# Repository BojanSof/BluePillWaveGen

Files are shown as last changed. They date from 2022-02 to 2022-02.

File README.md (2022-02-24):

# STM32 BluePill DDS WaveGen

DDS function generator implemented with STM32 BluePill board, based on
STM32F103C8T6 microcontroller, 8-bit R-2R ladder DAC and additional circuitry
for removing the DC offset.

The user interface is realized with OLED display based on SSD1306 controller and
incremental rotary encoder.

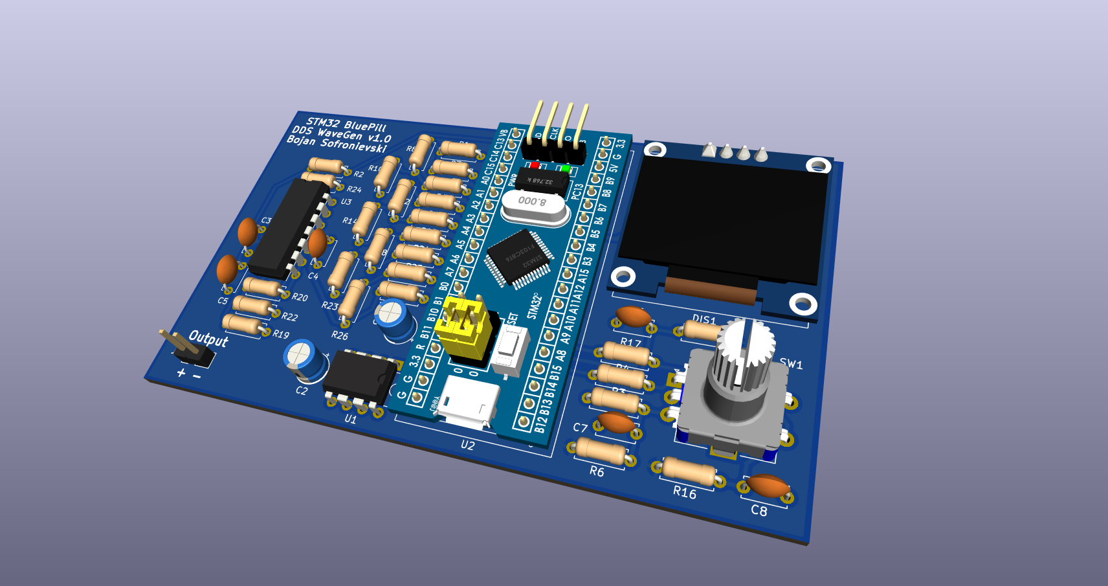
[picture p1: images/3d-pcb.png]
Kicad PCB 3D view


## Specs

Goal specs:

- Waveforms: sine, square, triangle, sawtooth (arbitrary waveforms can easily be
  added)
- Frequency: 0 - 35 kHz, frequncy resolution is variable
- Amplitude: 500 - 3000 mV (software control)

Additional tests and modifications should be done to reach the specs.

## Working Principle

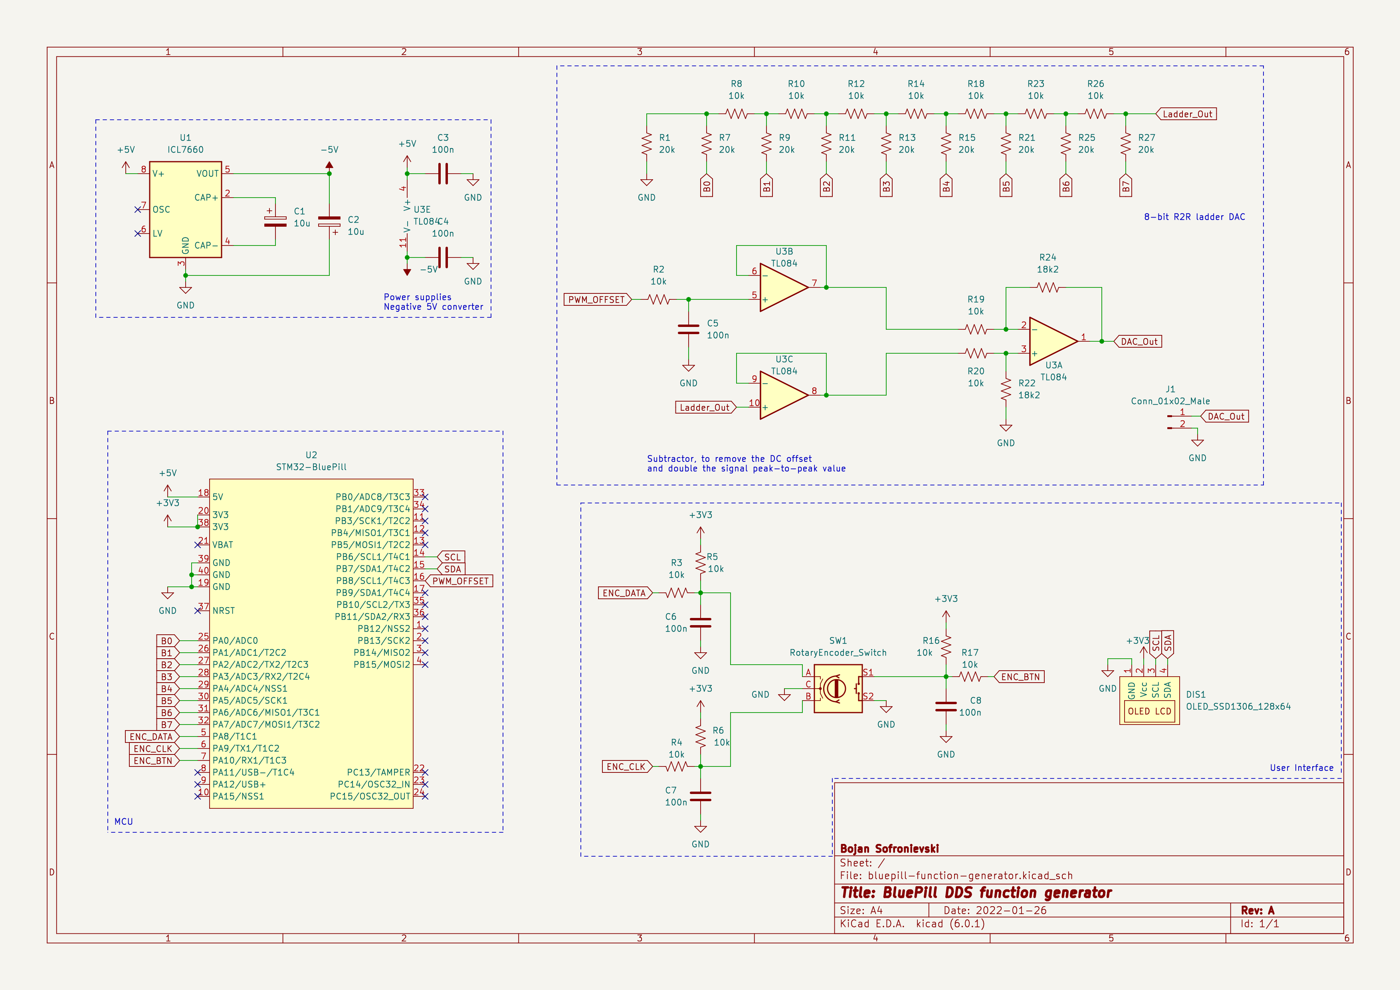
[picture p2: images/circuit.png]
WaveGen circuit


The MCU generates the data for the 8-bit R-2R ladder D/A converter.

Two of the op amps inside TL084 are used as voltage buffers, one for the output
of the DAC and the second one for the variable voltage generated by filtering
PWM signal outputed by the MCU.
This variable voltage is used to remove the DC offset of the generated waveform.
Removing the DC offset is realised with the third op amp, which subtracts the
output of the DAC and the variable voltage and multiplies this difference by
1.82 so the output signal has maximum amplitude of 3 V.

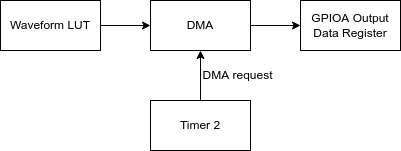
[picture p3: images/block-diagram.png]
DAC data generation


To generate the data for the DAC, each waveform has lookup table stored in the
Flash memory of the MCU, with 256 elements with size 1 byte.
The values stored in the table are actually the data that need to be fed into
the DAC.
During runtime, whole or part of the table is copied into SRAM of the MCU, based
on the frequency of the waveform.
By changing the LUT, arbitrary periodic waveforms can be generated.

Timer 2 of the MCU is configured to generate DMA request.
It has base clock of  14.4 MHz and the value stored in the Auto-Reload Register 
(ARR) depends on the  frequency of the waveform. The value for ARR is calculated
using the following formula:

<center>ARR=TIM2\_BaseClock/(L\*f) - 1</center>

where L is the size of the LUT stored in SRAM and f is the frequency of the
waveform.

The DMA unit transfers data from the LUT in SRAM to the GPIOA output data
register.
The pins PA0-PA7 are used to output the data to the DAC.
Because the output data register of GPIOA is used, the pins PA8-PA15 can not be
used as general purpose outputs, but can be used in the other modes.
This problem can be resolved by writing to the bit set reset register instead of
the output data register.

## Software

The software was written in C, using STM32 HAL library, in STM32CubeIDE.

I have also written SSD1306 driver which can be further developed to include
more functionalities.

The code also includes isntantenous rotational speed measurement for the rotary
encoder with goal to change the values for frequency and amplitude based on the
rotational speed, i.e. faster turning of the encoder results in greater change
of the value.
This part of the code should also be improved, for better user experience.

## Experimental results

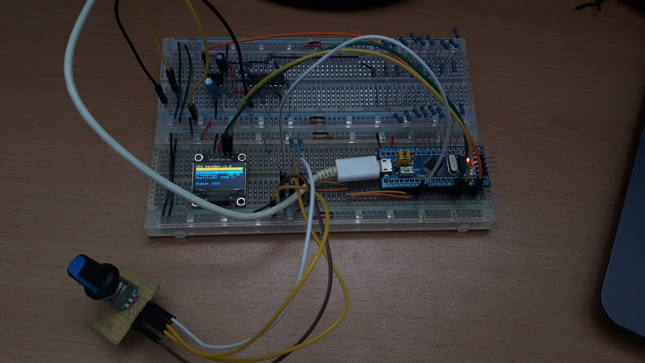
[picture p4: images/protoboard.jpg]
Protoboard version


The following waveforms are measured with DSO150 oscilloscope.

<table>
  <tr>
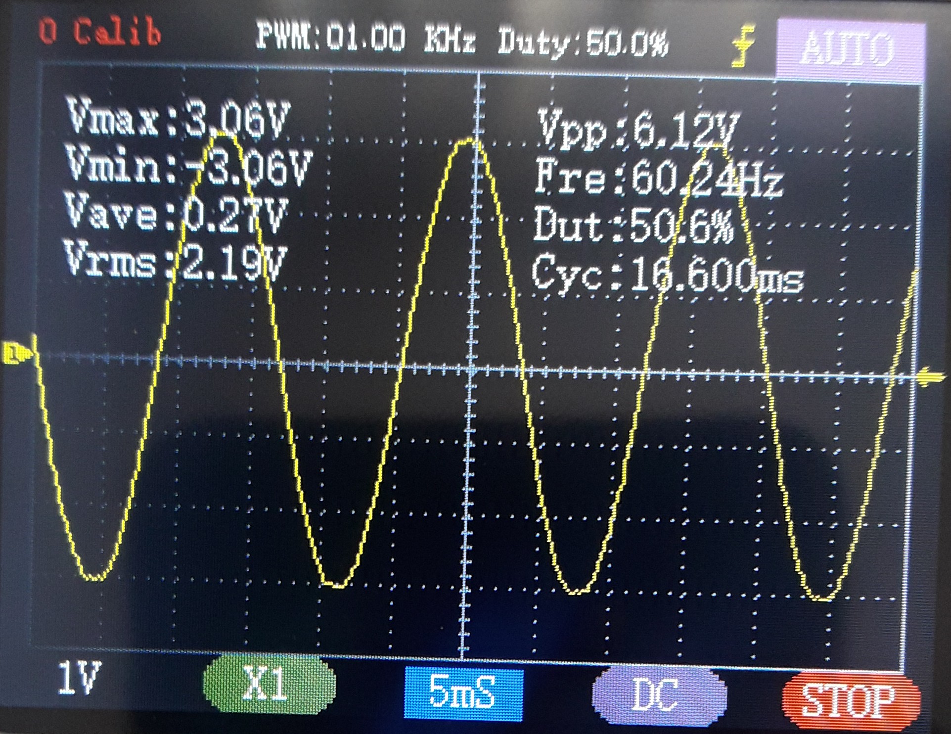
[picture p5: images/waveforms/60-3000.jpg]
Sine 60 Hz 3000 mV
    <td> </td>
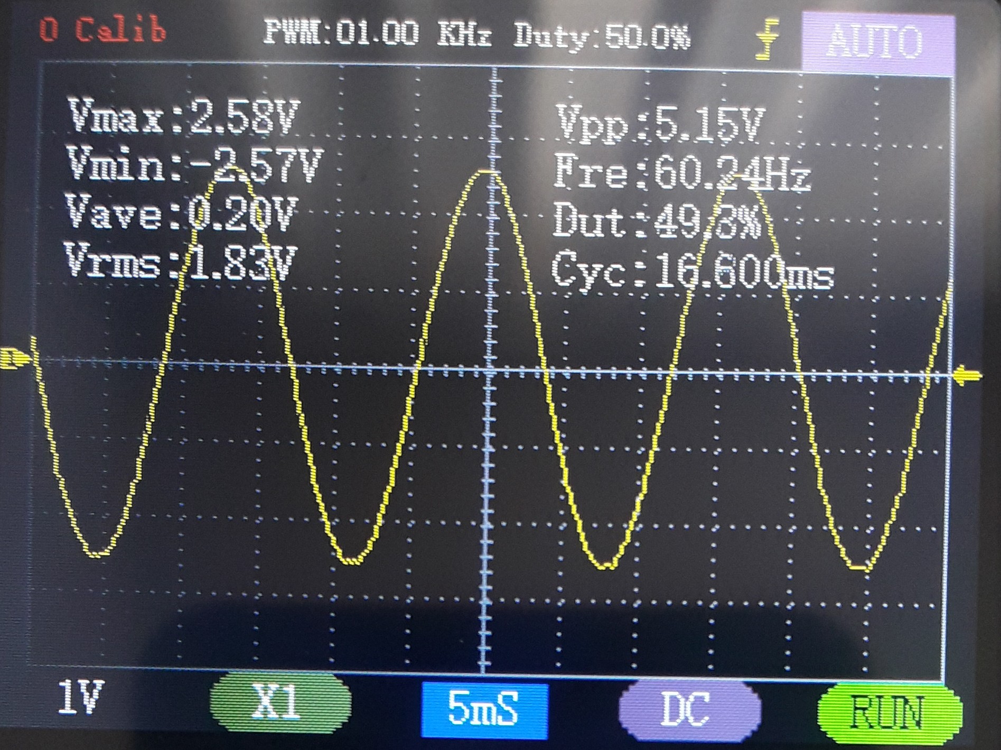
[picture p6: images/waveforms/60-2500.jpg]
Sine 60 Hz 2500 mV
    <td> </td>
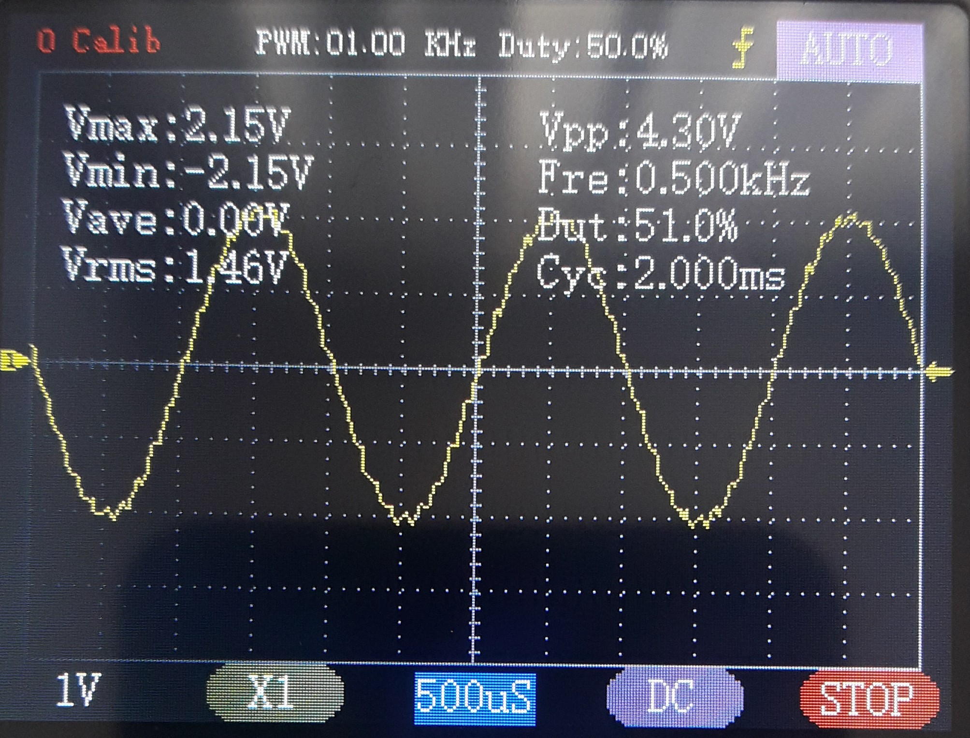
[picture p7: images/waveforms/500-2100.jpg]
Sine 500 Hz 2100 mV
    <td> </td>
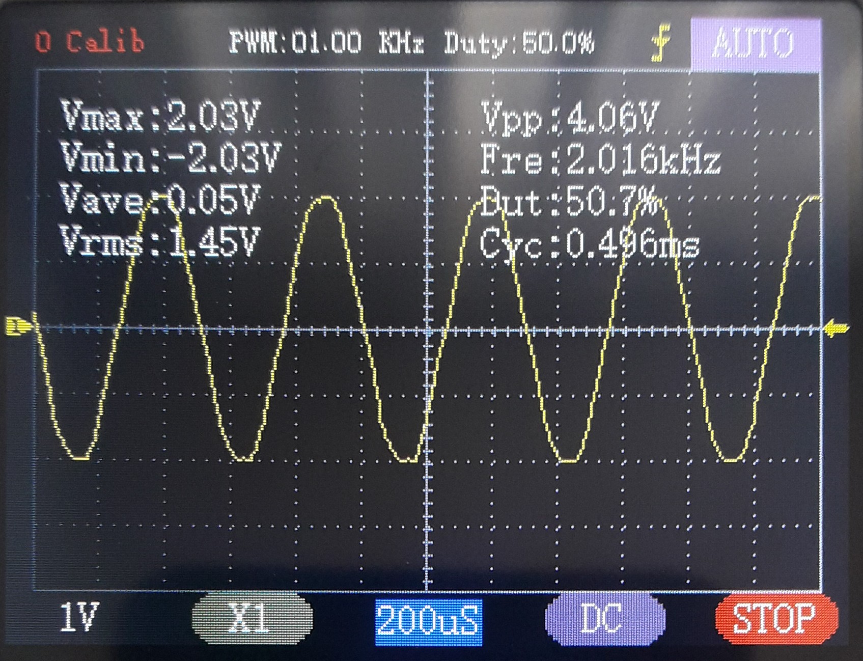
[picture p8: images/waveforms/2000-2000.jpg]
Sine 2000 Hz 2000 mV
    <td> </td>
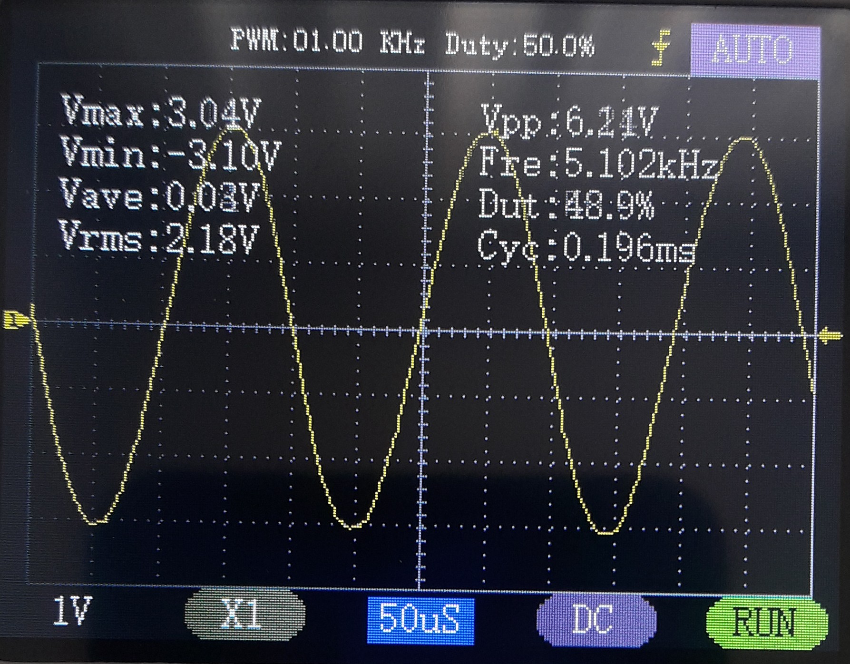
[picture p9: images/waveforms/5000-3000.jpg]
Sine 5000 Hz 3000 mV
    <td> </td>
  </tr> 
  <tr>
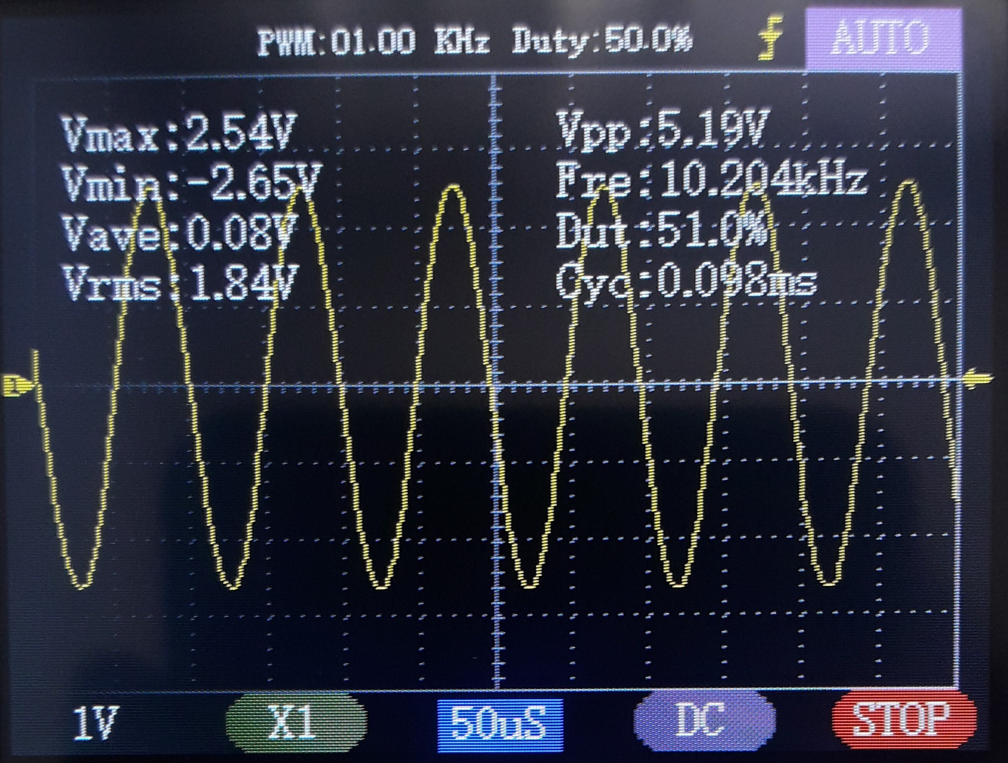
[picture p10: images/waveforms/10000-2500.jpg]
Sine 10000 Hz 2500 mv
    <td> </td>
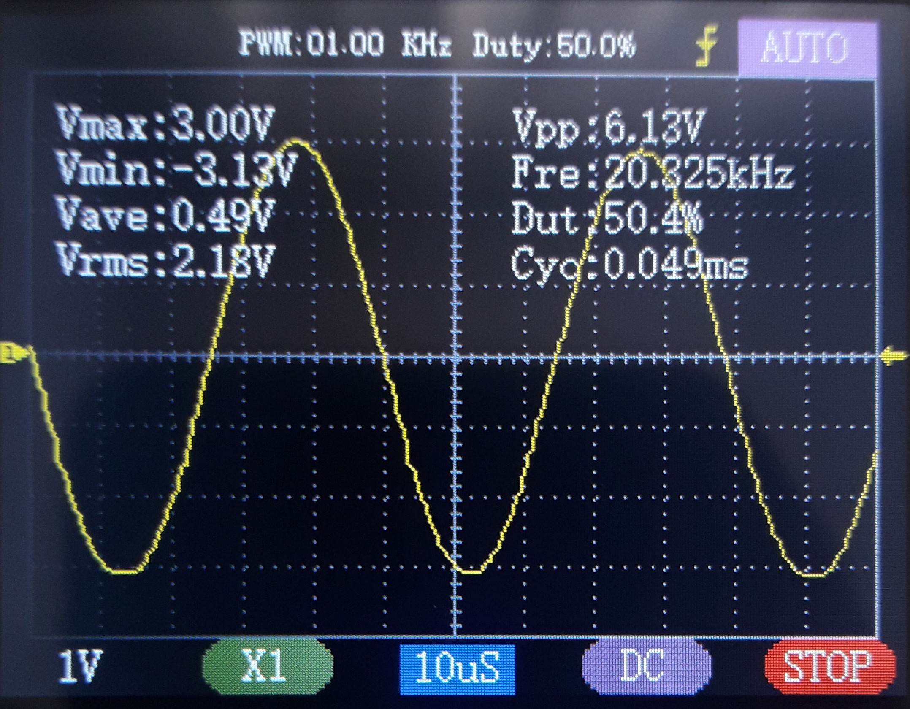
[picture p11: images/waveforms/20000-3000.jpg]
Sine 20000 Hz 3000 mv
    <td> </td>
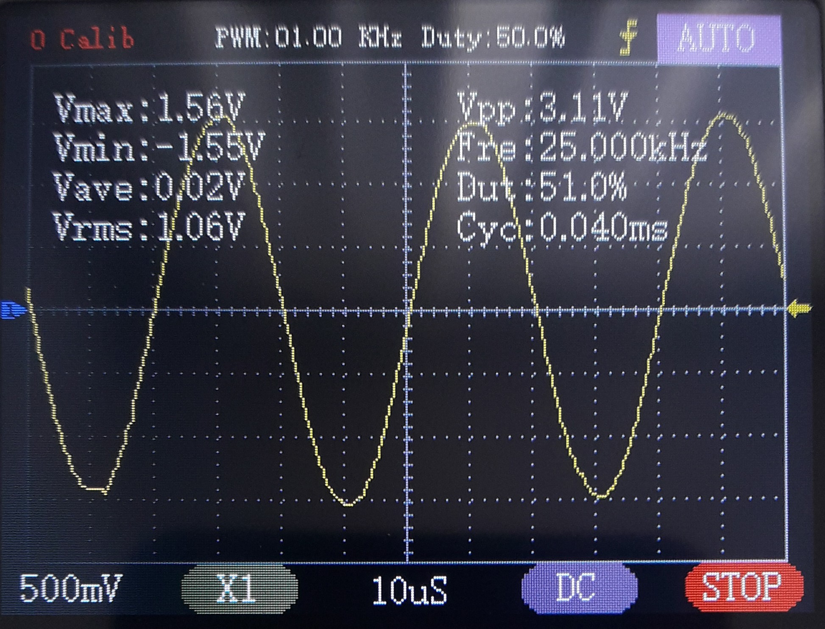
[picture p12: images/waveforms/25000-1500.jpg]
Sine 25000 Hz 1500 mv
    <td> </td>
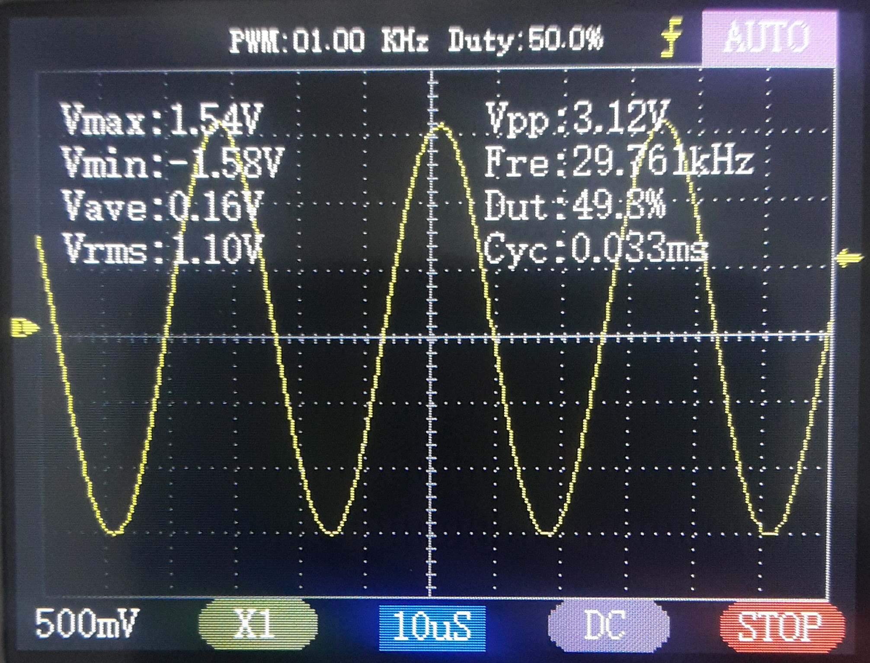
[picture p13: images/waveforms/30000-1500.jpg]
Sine 30000 Hz 1500 mv
    <td> </td>
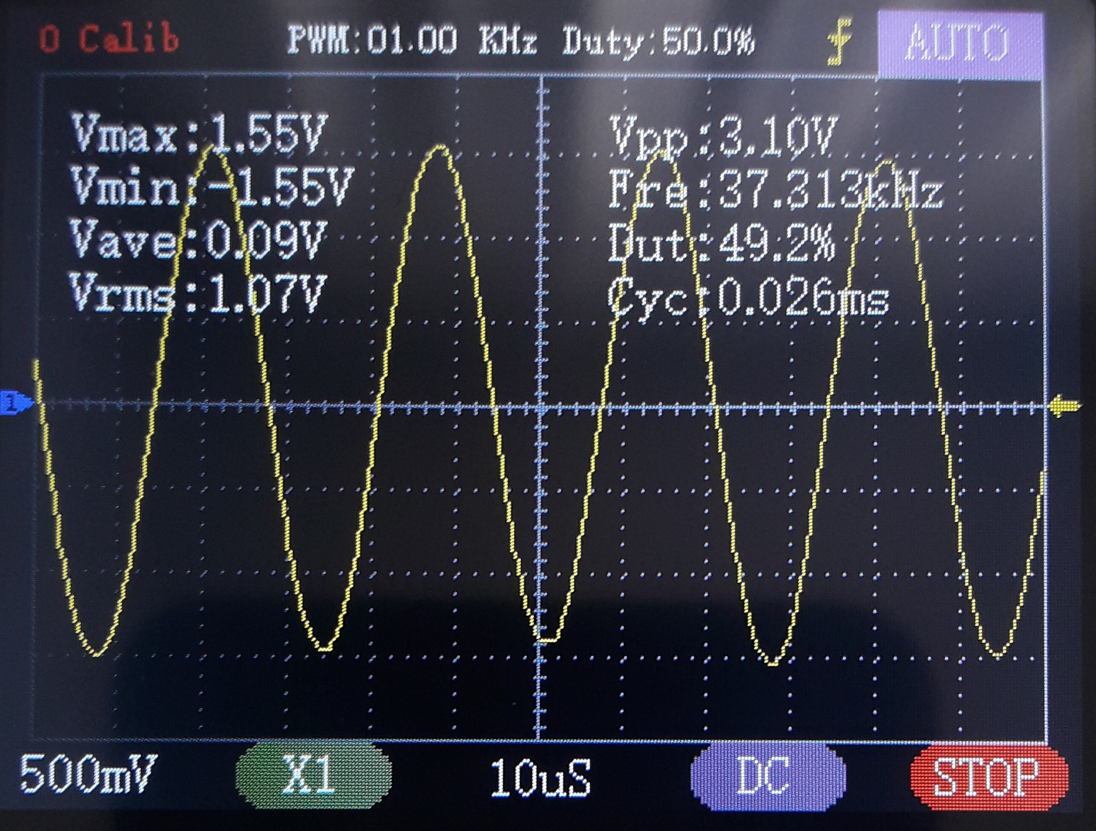
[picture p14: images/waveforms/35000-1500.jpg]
Sine 35000 Hz 1500 mv
    <td> </td>
  </tr> 
  <tr>
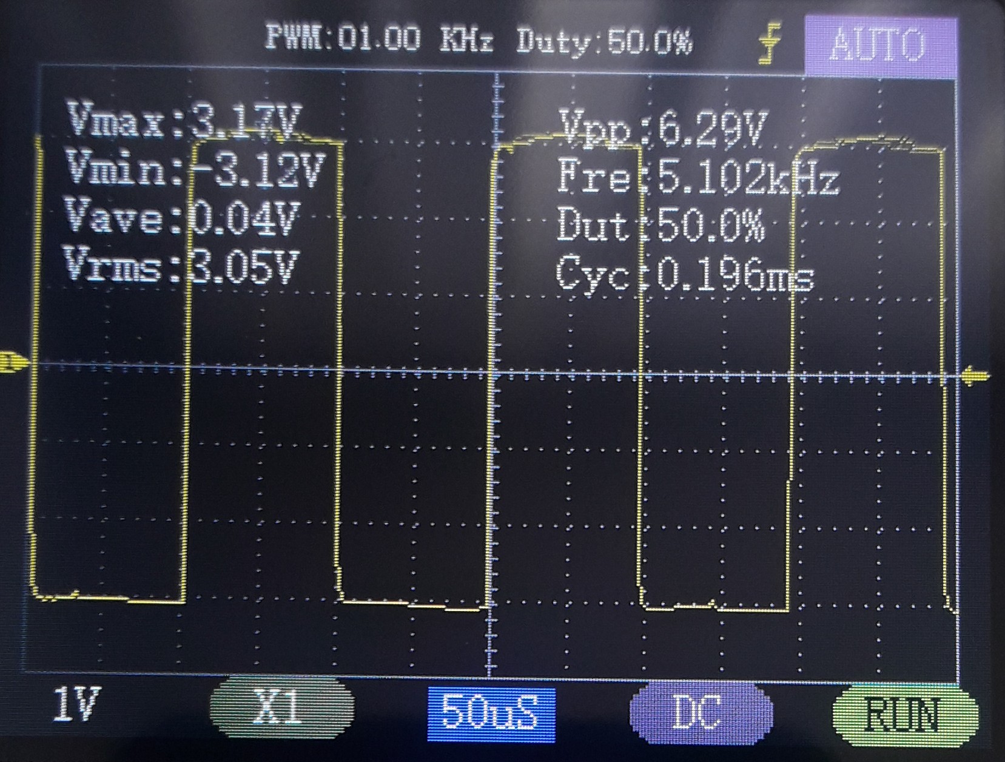
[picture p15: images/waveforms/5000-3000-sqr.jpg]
Square 5000 Hz 3000 mv
    <td> </td>
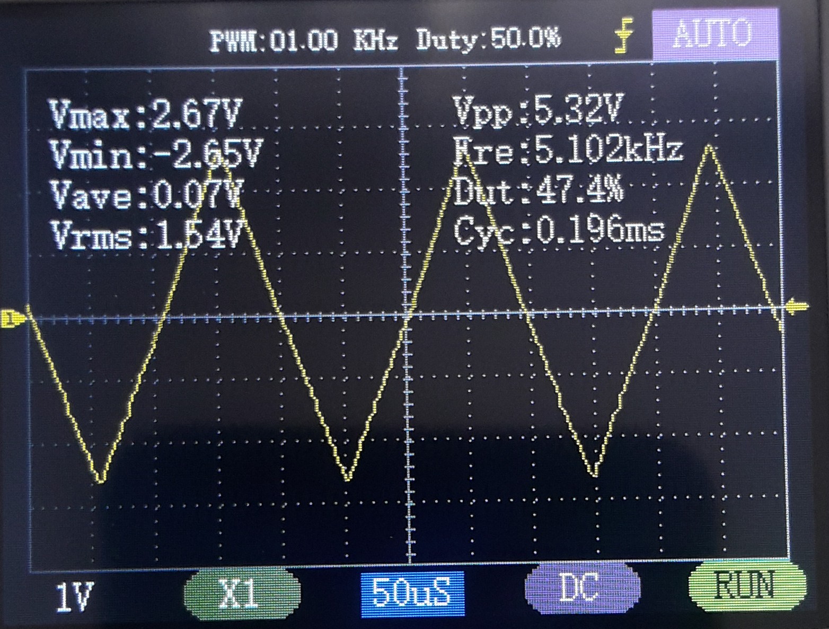
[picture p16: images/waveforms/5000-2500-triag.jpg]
Triangle 5000 Hz 2500 mv
    <td> </td>
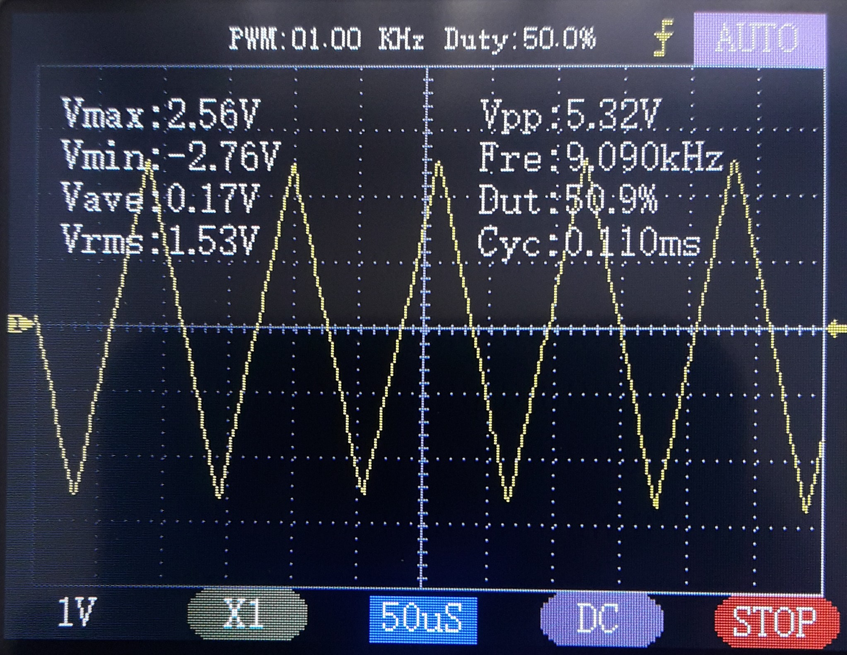
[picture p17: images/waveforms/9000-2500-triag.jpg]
Triangle 9000 Hz 2500 mv
    <td> </td>
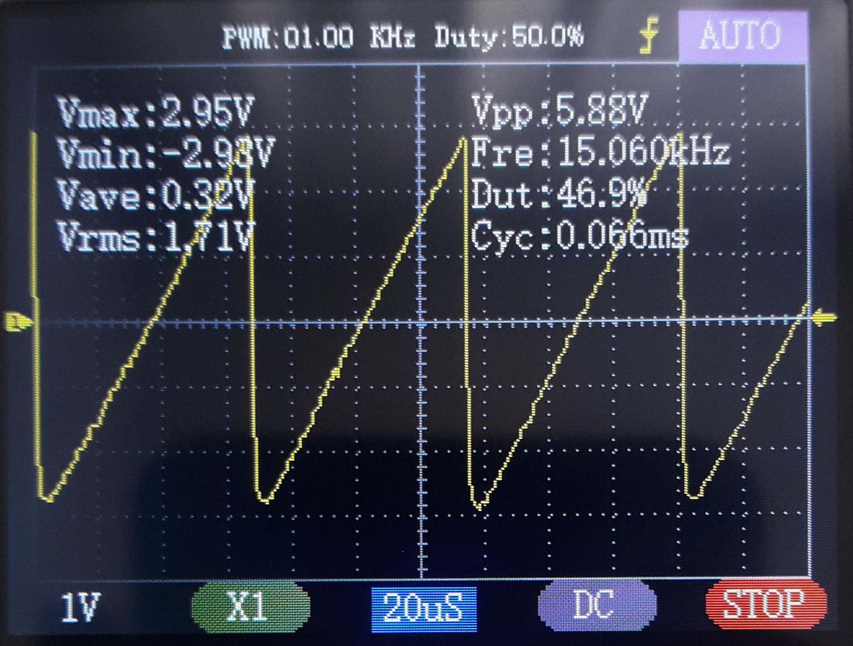
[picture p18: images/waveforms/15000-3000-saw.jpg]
Sawtooth 15000 Hz 3000 mv
    <td> </td>
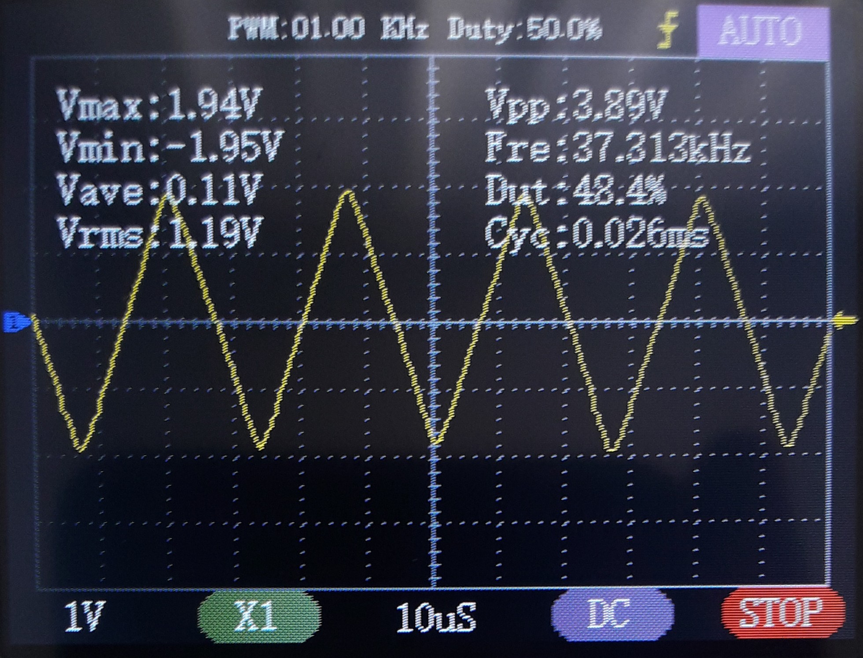
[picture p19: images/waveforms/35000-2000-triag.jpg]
Triangle 35000 Hz 2000 mv
    <td> </td>
  </tr> 
</table>

## Further improvements

- Additional tests and calibration to conclude the frequency and amplitude resolution
- USB virtual serial port to transfer LUT data for arbitrary waveform
- Low-pass filter after DAC output

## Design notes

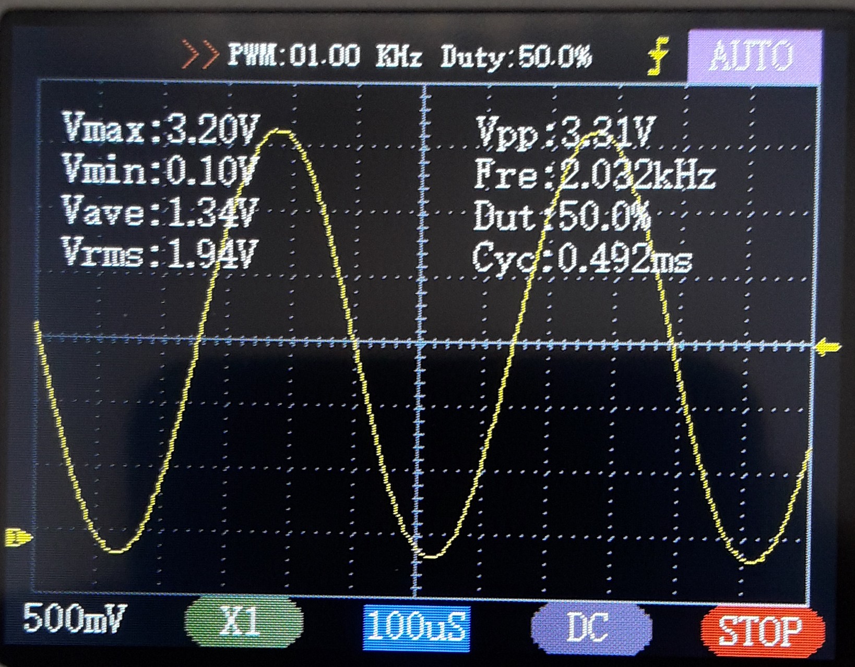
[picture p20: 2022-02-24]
images/waveforms/2000-r2r.jpg

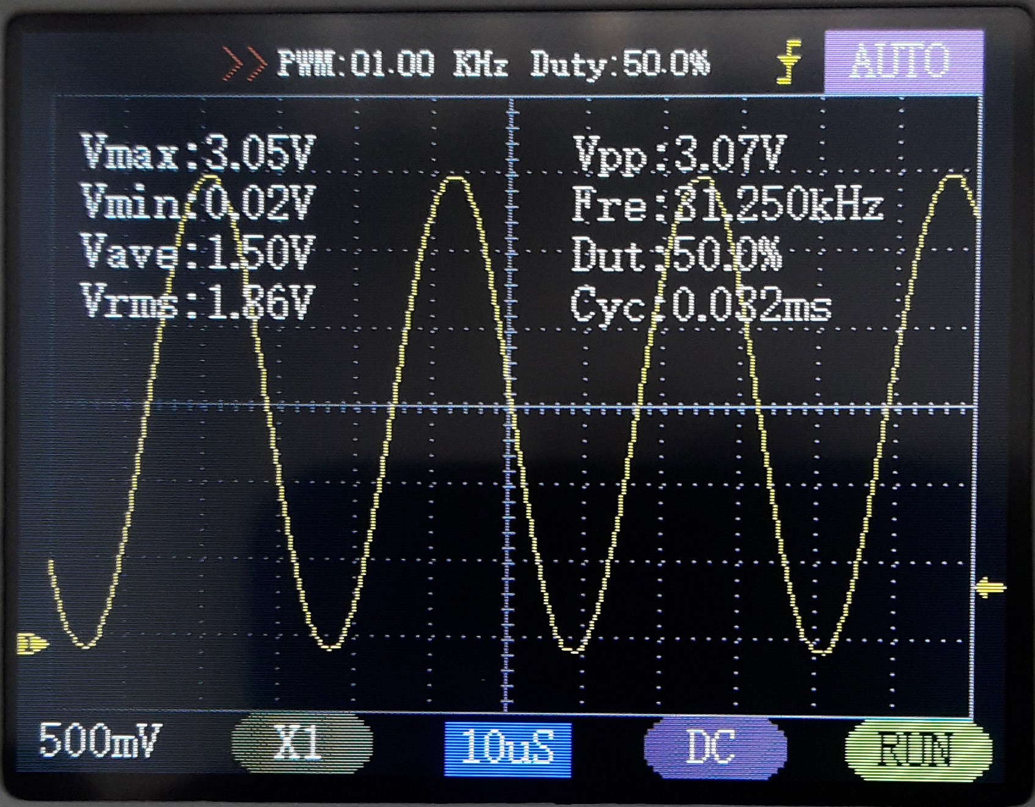
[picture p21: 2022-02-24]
images/waveforms/29900-r2r.jpg

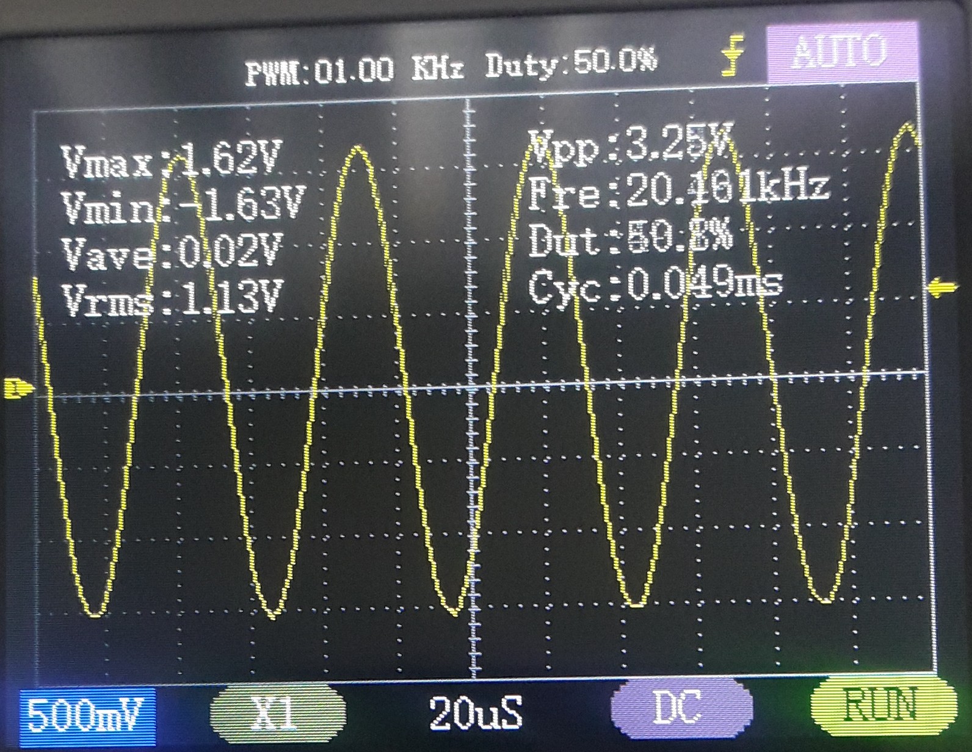
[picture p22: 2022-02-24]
images/waveforms/20000-r2r.jpg

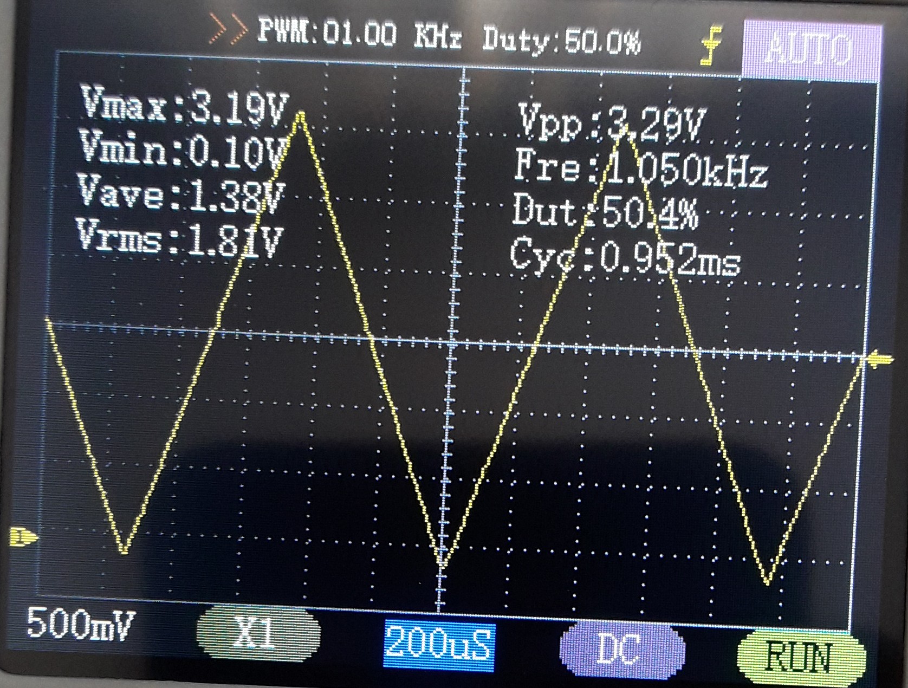
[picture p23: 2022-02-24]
images/waveforms/1050-r2r-triag.jpg

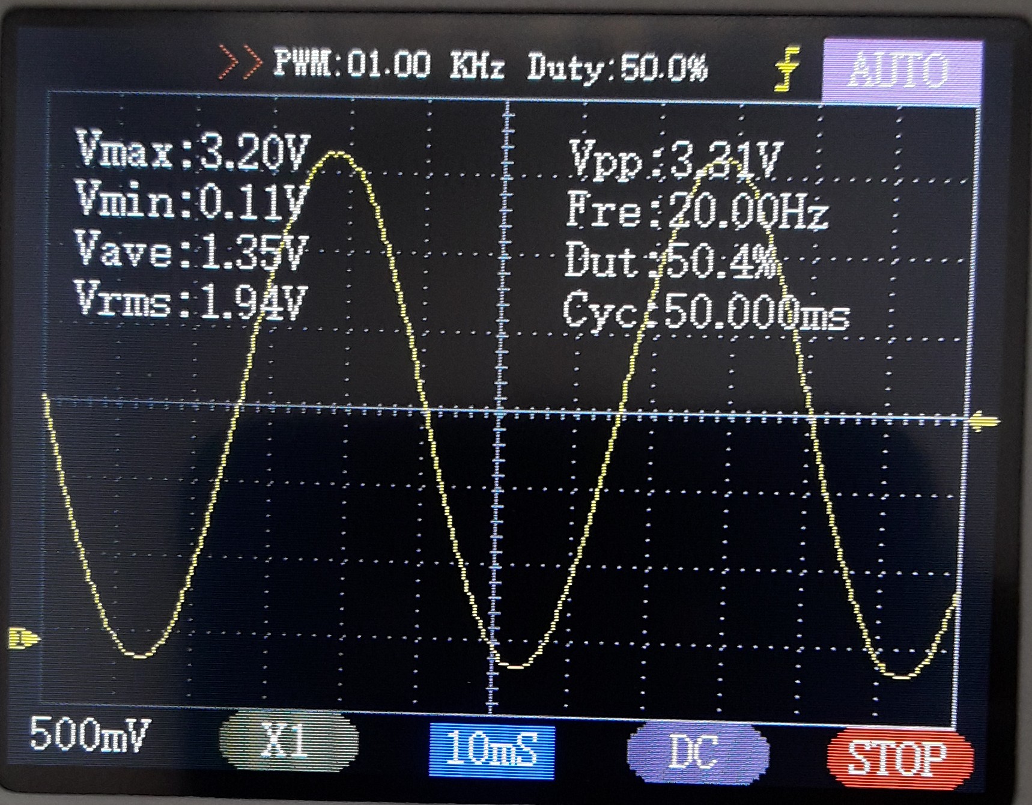
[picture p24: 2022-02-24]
images/waveforms/20-r2r.jpg

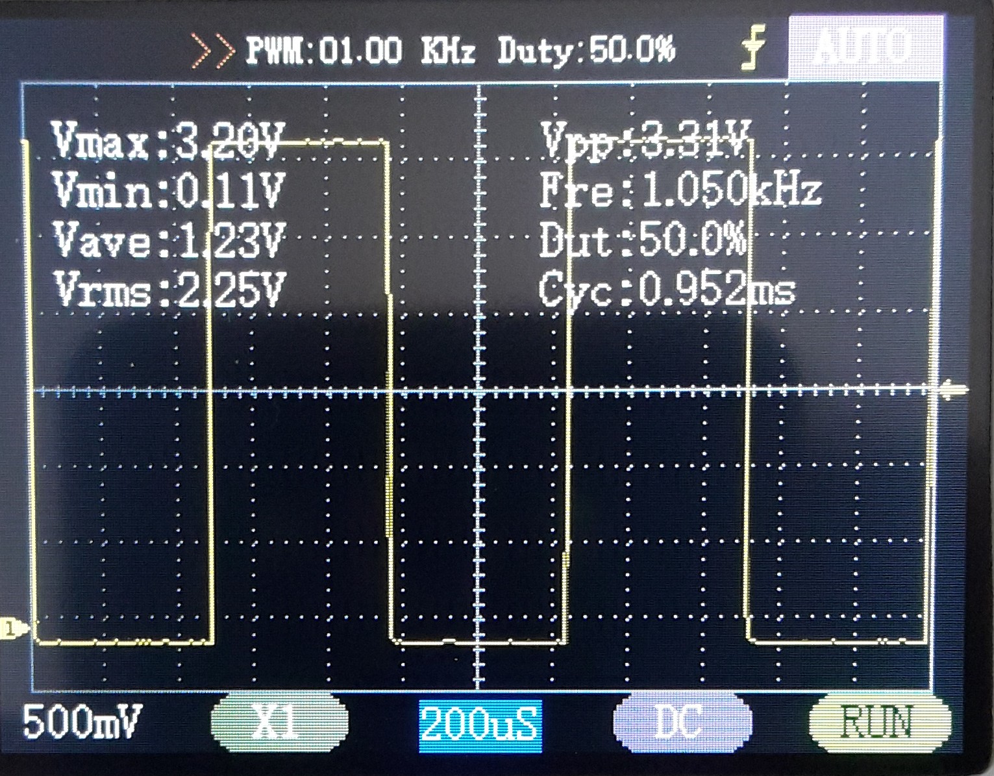
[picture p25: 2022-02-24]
images/waveforms/1050-r2r-sqr.jpg

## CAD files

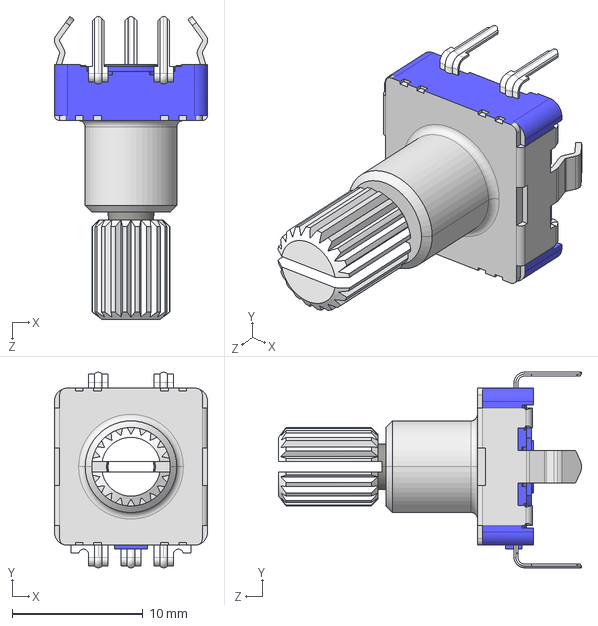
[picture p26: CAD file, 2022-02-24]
kicad/bluepill-function-generator/3d-models/RotaryEncoder/EC11RotaryEncoderSwitch-15mm.STEP
11.7 x 15.0 x 23.2 mm

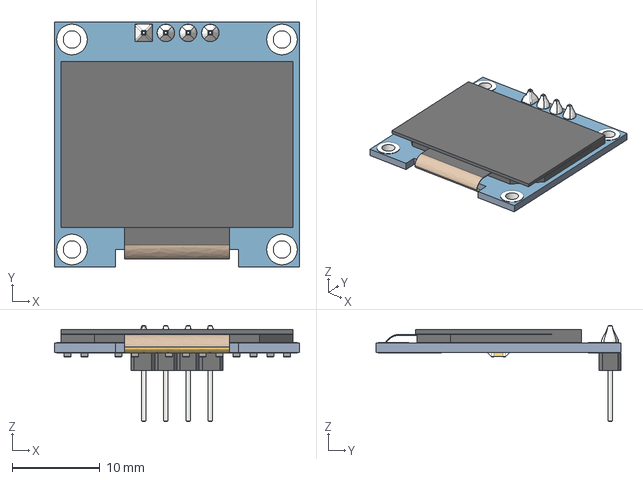
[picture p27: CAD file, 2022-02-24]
kicad/bluepill-function-generator/3d-models/SSD1306-OLED-I2C/OLEDv3.step
28.0 x 28.0 x 11.0 mm

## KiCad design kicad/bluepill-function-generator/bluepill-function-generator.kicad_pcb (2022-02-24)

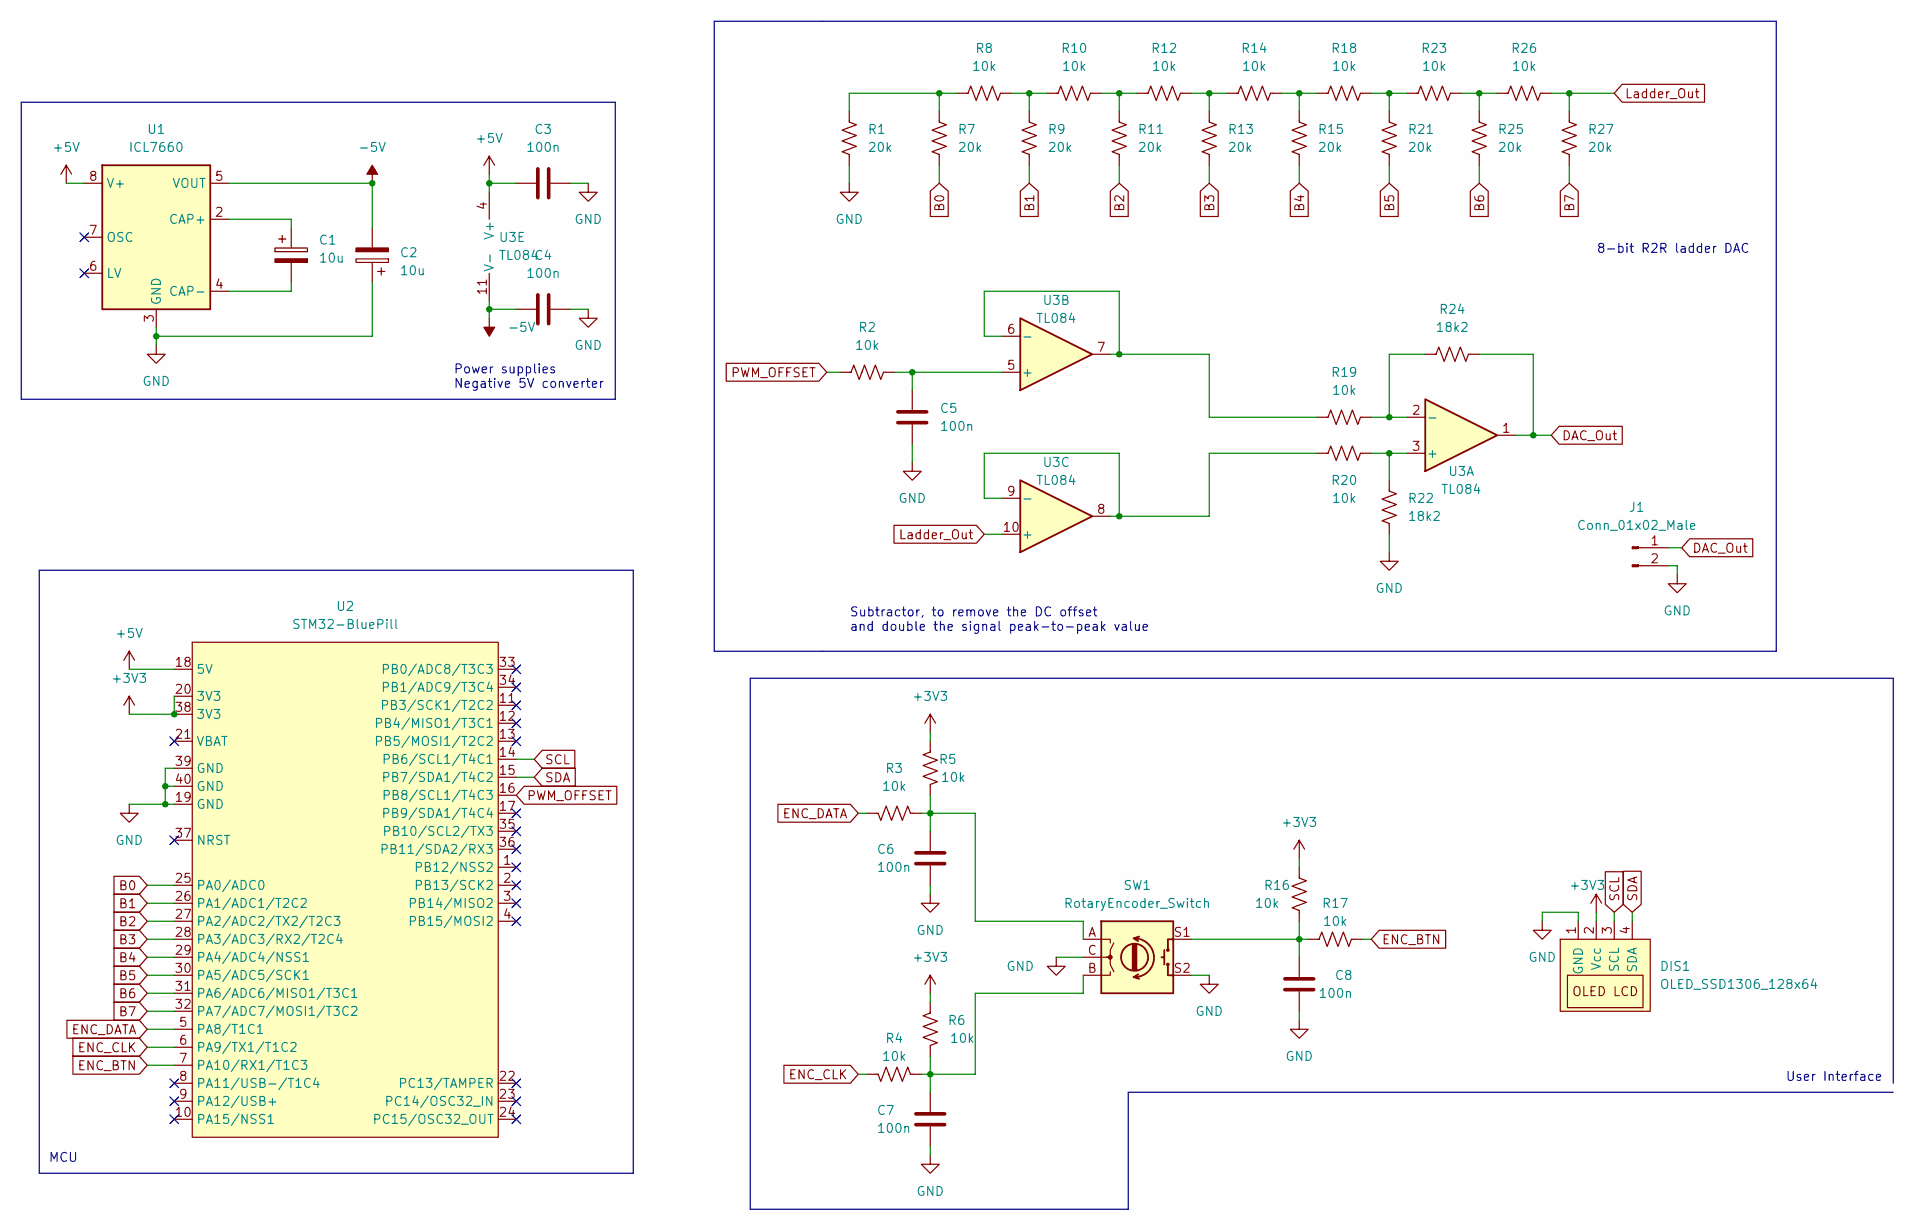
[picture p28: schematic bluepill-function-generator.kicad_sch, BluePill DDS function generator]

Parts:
C1, C2: 10u; CP_Radial_D5.0mm_P2.50mm
C3, C4, C5, C6, C7, C8: 100n; C_Disc_D5.0mm_W2.5mm_P5.00mm
DIS1: OLED_SSD1306_128x64; OLED-SSD1306-128x64
J1: Conn_01x02_Male; PinHeader_1x02_P2.54mm_Vertical
R1, R7, R9, R11, R13, R15, R21, R25, R27: 20k; R_Axial_DIN0207_L6.3mm_D2.5mm_P7.62mm_Horizontal
R2, R3, R4, R5, R6, R8, R10, R12, R14, R16, R17, R18, R19, R20, R23, R26: 10k; R_Axial_DIN0207_L6.3mm_D2.5mm_P7.62mm_Horizontal
R22, R24: 18k2; R_Axial_DIN0207_L6.3mm_D2.5mm_P7.62mm_Horizontal
SW1: RotaryEncoder_Switch; RotaryEncoder_Alps_EC11E-Switch_Vertical_H20mm
U1: ICL7660; DIP-8_W7.62mm
U2: STM32-BluePill
U3: TL084; DIP-14_W7.62mm

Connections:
+3V3: DIS1.2 (Vcc), R5.2, R6.2, R16.2, U2.20 (3V3), U2.38 (3V3)
+5V: C3.1, U1.8 (V+), U2.18 (5V), U3.4 (V+)
-5V: C2.2, C4.1, U1.5 (VOUT), U3.11 (V-)
B0: R7.2, U2.25 (PA0/ADC0)
B1: R9.1, U2.26 (PA1/ADC1/T2C2)
B2: R11.2, U2.27 (PA2/ADC2/TX2/T2C3)
B3: R13.1, U2.28 (PA3/ADC3/RX2/T2C4)
B4: R15.2, U2.29 (PA4/ADC4/NSS1)
B5: R21.1, U2.30 (PA5/ADC5/SCK1)
B6: R25.2, U2.31 (PA6/ADC6/MISO1/T3C1)
B7: R27.2, U2.32 (PA7/ADC7/MOSI1/T3C2)
DAC_Out: J1.1, R24.1, U3.1
ENC_BTN: R17.1, U2.7 (PA10/RX1/T1C3)
ENC_CLK: R4.1, U2.6 (PA9/TX1/T1C2)
ENC_DATA: R3.2, U2.5 (PA8/T1C1)
GND: C2.1, C3.2, C4.2, C5.1, C6.2, C7.2, C8.2, DIS1.1 (GND), J1.2, R1.1, R22.2, SW1.C, SW1.S2, U1.3 (GND), U2.19 (GND), U2.39 (GND), U2.40 (GND)
Ladder_Out: R26.1, R27.1, U3.10 (+)
unnamed: C1.1, U1.2 (CAP+)
unnamed: C1.2, U1.4 (CAP-)
unnamed: C5.2, R2.2, U3.5 (+)
unnamed: C6.1, R3.1, R5.1, SW1.A
unnamed: C7.1, R4.2, R6.1, SW1.B
unnamed: C8.1, R16.1, R17.2, SW1.S1
unnamed: R1.2, R7.1, R8.2
unnamed: R10.1, R11.1, R12.2
unnamed: R8.1, R9.2, R10.2
unnamed: R12.1, R13.2, R14.2
unnamed: R14.1, R15.1, R18.2
unnamed: R18.1, R21.2, R23.2
unnamed: R19.1, R24.2, U3.2 (-)
unnamed: R19.2, U3.6 (-), U3.7
unnamed: R20.1, R22.1, U3.3 (+)
unnamed: R20.2, U3.8, U3.9 (-)
unnamed: R23.1, R25.1, R26.2
PWM_OFFSET: R2.1, U2.16 (PB8/SCL1/T4C3)
SCL: DIS1.3 (SCL), U2.14 (PB6/SCL1/T4C1)
SDA: DIS1.4 (SDA), U2.15 (PB7/SDA1/T4C2)

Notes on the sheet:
8-bit R2R ladder DAC
User Interface
MCU
Subtractor, to remove the DC offset and double the signal peak-to-peak value
Power supplies Negative 5V converter

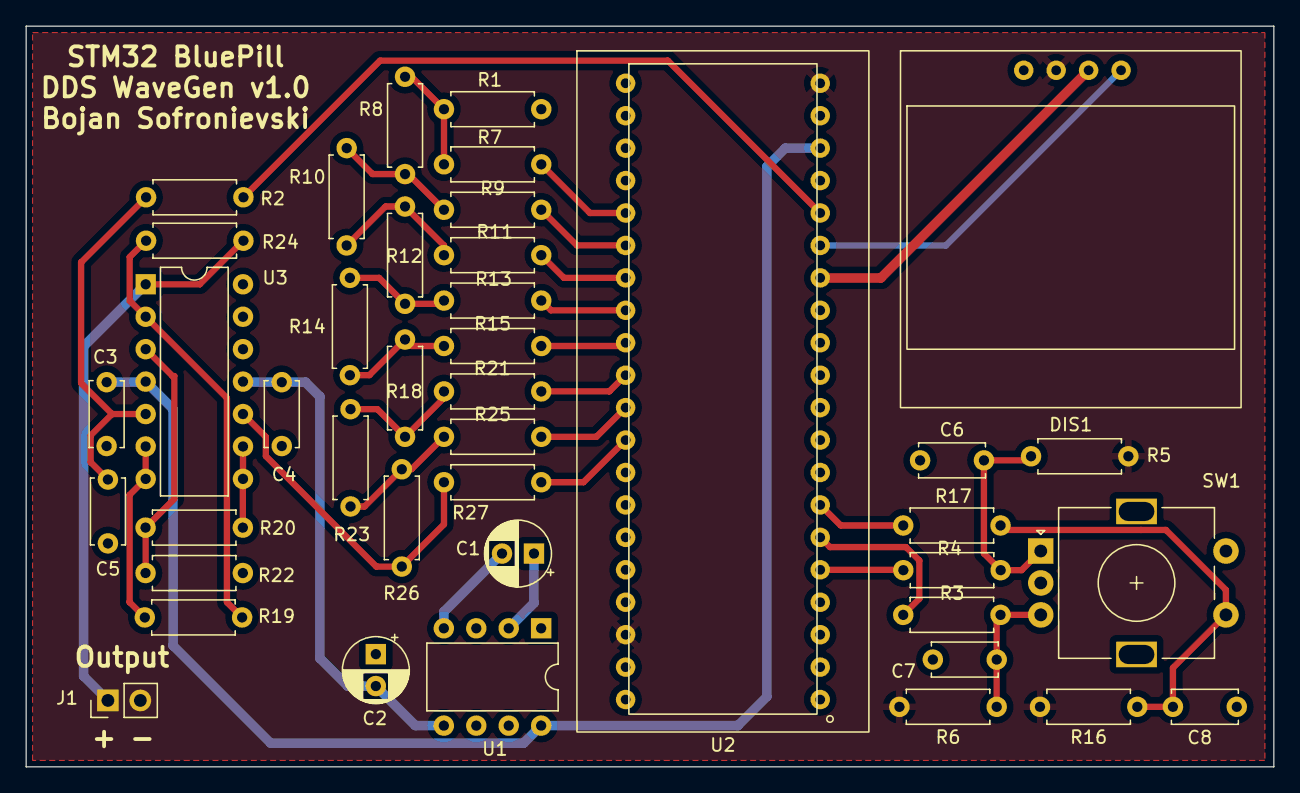
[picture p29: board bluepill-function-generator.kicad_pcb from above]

Board: 2 copper layers, 97.7 x 58.0 mm, 41 parts (0 on the bottom side), 37 nets.

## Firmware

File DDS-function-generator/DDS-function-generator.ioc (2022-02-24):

#MicroXplorer Configuration settings - do not modify
Dma.Request0=TIM2_UP
Dma.RequestsNb=1
Dma.TIM2_UP.0.Direction=DMA_MEMORY_TO_PERIPH
Dma.TIM2_UP.0.Instance=DMA1_Channel2
Dma.TIM2_UP.0.MemDataAlignment=DMA_MDATAALIGN_BYTE
Dma.TIM2_UP.0.MemInc=DMA_MINC_ENABLE
Dma.TIM2_UP.0.Mode=DMA_CIRCULAR
Dma.TIM2_UP.0.PeriphDataAlignment=DMA_PDATAALIGN_BYTE
Dma.TIM2_UP.0.PeriphInc=DMA_PINC_DISABLE
Dma.TIM2_UP.0.Priority=DMA_PRIORITY_VERY_HIGH
Dma.TIM2_UP.0.RequestParameters=Instance,Direction,PeriphInc,MemInc,PeriphDataAlignment,MemDataAlignment,Mode,Priority
File.Version=6
GPIO.groupedBy=Group By Peripherals
KeepUserPlacement=false
Mcu.Family=STM32F1
Mcu.IP0=DMA
Mcu.IP1=I2C1
Mcu.IP2=NVIC
Mcu.IP3=RCC
Mcu.IP4=SYS
Mcu.IP5=TIM1
Mcu.IP6=TIM2
Mcu.IP7=TIM3
Mcu.IP8=TIM4
Mcu.IPNb=9
Mcu.Name=STM32F103C(8-B)Tx
Mcu.Package=LQFP48
Mcu.Pin0=PD0-OSC_IN
Mcu.Pin1=PD1-OSC_OUT
Mcu.Pin10=PB0
Mcu.Pin11=PB1
Mcu.Pin12=PA8
Mcu.Pin13=PA9
Mcu.Pin14=PA10
Mcu.Pin15=PA13
Mcu.Pin16=PA14
Mcu.Pin17=PB6
Mcu.Pin18=PB7
Mcu.Pin19=PB8
Mcu.Pin2=PA0-WKUP
Mcu.Pin20=VP_SYS_VS_Systick
Mcu.Pin21=VP_TIM2_VS_ClockSourceINT
Mcu.Pin22=VP_TIM3_VS_ClockSourceINT
Mcu.Pin3=PA1
Mcu.Pin4=PA2
Mcu.Pin5=PA3
Mcu.Pin6=PA4
Mcu.Pin7=PA5
Mcu.Pin8=PA6
Mcu.Pin9=PA7
Mcu.PinsNb=23
Mcu.ThirdPartyNb=0
Mcu.UserConstants=
Mcu.UserName=STM32F103C8Tx
MxCube.Version=6.3.0
MxDb.Version=DB.6.0.30
NVIC.BusFault_IRQn=true\:0\:0\:false\:false\:true\:false\:false
NVIC.DMA1_Channel2_IRQn=true\:0\:0\:false\:false\:true\:false\:true
NVIC.DebugMonitor_IRQn=true\:0\:0\:false\:false\:true\:false\:false
NVIC.ForceEnableDMAVector=true
NVIC.HardFault_IRQn=true\:0\:0\:false\:false\:true\:false\:false
NVIC.MemoryManagement_IRQn=true\:0\:0\:false\:false\:true\:false\:false
NVIC.NonMaskableInt_IRQn=true\:0\:0\:false\:false\:true\:false\:false
NVIC.PendSV_IRQn=true\:0\:0\:false\:false\:true\:false\:false
NVIC.PriorityGroup=NVIC_PRIORITYGROUP_4
NVIC.SVCall_IRQn=true\:0\:0\:false\:false\:true\:false\:false
NVIC.SysTick_IRQn=true\:15\:0\:false\:false\:true\:false\:true
NVIC.TIM3_IRQn=true\:0\:0\:false\:false\:true\:true\:true
NVIC.UsageFault_IRQn=true\:0\:0\:false\:false\:true\:false\:false
PA0-WKUP.GPIOParameters=GPIO_Speed,GPIO_Label
PA0-WKUP.GPIO_Label=DAC0
PA0-WKUP.GPIO_Speed=GPIO_SPEED_FREQ_HIGH
PA0-WKUP.Locked=true
PA0-WKUP.Signal=GPIO_Output
PA1.GPIOParameters=GPIO_Speed,GPIO_Label
PA1.GPIO_Label=DAC1
PA1.GPIO_Speed=GPIO_SPEED_FREQ_HIGH
PA1.Locked=true
PA1.Signal=GPIO_Output
PA10.GPIOParameters=GPIO_Label
PA10.GPIO_Label=ENC_BTN
PA10.Locked=true
PA10.Signal=GPIO_Input
PA13.Mode=Serial_Wire
PA13.Signal=SYS_JTMS-SWDIO
PA14.Mode=Serial_Wire
PA14.Signal=SYS_JTCK-SWCLK
PA2.GPIOParameters=GPIO_Speed,GPIO_Label
PA2.GPIO_Label=DAC2
PA2.GPIO_Speed=GPIO_SPEED_FREQ_HIGH
PA2.Locked=true
PA2.Signal=GPIO_Output
PA3.GPIOParameters=GPIO_Speed,GPIO_Label
PA3.GPIO_Label=DAC3
PA3.GPIO_Speed=GPIO_SPEED_FREQ_HIGH
PA3.Locked=true
PA3.Signal=GPIO_Output
PA4.GPIOParameters=GPIO_Speed,GPIO_Label
PA4.GPIO_Label=DAC4
PA4.GPIO_Speed=GPIO_SPEED_FREQ_HIGH
PA4.Locked=true
PA4.Signal=GPIO_Output
PA5.GPIOParameters=GPIO_Speed,GPIO_Label
PA5.GPIO_Label=DAC5
PA5.GPIO_Speed=GPIO_SPEED_FREQ_HIGH
PA5.Locked=true
PA5.Signal=GPIO_Output
PA6.GPIOParameters=GPIO_Speed,GPIO_Label
PA6.GPIO_Label=DAC6
PA6.GPIO_Speed=GPIO_SPEED_FREQ_HIGH
PA6.Locked=true
PA6.Signal=GPIO_Output
PA7.GPIOParameters=GPIO_Speed,GPIO_Label
PA7.GPIO_Label=DAC7
PA7.GPIO_Speed=GPIO_SPEED_FREQ_HIGH
PA7.Locked=true
PA7.Signal=GPIO_Output
PA8.Signal=S_TIM1_CH1
PA9.Signal=S_TIM1_CH2
PB0.Locked=true
PB0.Signal=GPIO_Output
PB1.Locked=true
PB1.Signal=GPIO_Output
PB6.Mode=I2C
PB6.Signal=I2C1_SCL
PB7.Mode=I2C
PB7.Signal=I2C1_SDA
PB8.Signal=S_TIM4_CH3
PD0-OSC_IN.Mode=HSE-External-Oscillator
PD0-OSC_IN.Signal=RCC_OSC_IN
PD1-OSC_OUT.Mode=HSE-External-Oscillator
PD1-OSC_OUT.Signal=RCC_OSC_OUT
PinOutPanel.RotationAngle=0
ProjectManager.AskForMigrate=true
ProjectManager.BackupPrevious=false
ProjectManager.CompilerOptimize=6
ProjectManager.ComputerToolchain=false
ProjectManager.CoupleFile=true
ProjectManager.CustomerFirmwarePackage=
ProjectManager.DefaultFWLocation=true
ProjectManager.DeletePrevious=true
ProjectManager.DeviceId=STM32F103C8Tx
ProjectManager.FirmwarePackage=STM32Cube FW_F1 V1.8.4
ProjectManager.FreePins=false
ProjectManager.HalAssertFull=false
ProjectManager.HeapSize=0x200
ProjectManager.KeepUserCode=true
ProjectManager.LastFirmware=true
ProjectManager.LibraryCopy=1
ProjectManager.MainLocation=Core/Src
ProjectManager.NoMain=false
ProjectManager.PreviousToolchain=
ProjectManager.ProjectBuild=false
ProjectManager.ProjectFileName=DDS-function-generator.ioc
ProjectManager.ProjectName=DDS-function-generator
ProjectManager.RegisterCallBack=
ProjectManager.StackSize=0x400
ProjectManager.TargetToolchain=STM32CubeIDE
ProjectManager.ToolChainLocation=
ProjectManager.UnderRoot=true
ProjectManager.functionlistsort=1-SystemClock_Config-RCC-false-HAL-false,2-MX_GPIO_Init-GPIO-false-HAL-true,3-MX_DMA_Init-DMA-false-HAL-true,4-MX_TIM2_Init-TIM2-false-HAL-true,5-MX_TIM1_Init-TIM1-false-HAL-true,6-MX_TIM3_Init-TIM3-false-HAL-true,7-MX_I2C1_Init-I2C1-false-HAL-true
RCC.ADCFreqValue=36000000
RCC.AHBFreq_Value=72000000
RCC.APB1CLKDivider=RCC_HCLK_DIV2
RCC.APB1Freq_Value=36000000
RCC.APB1TimFreq_Value=72000000
RCC.APB2Freq_Value=72000000
RCC.APB2TimFreq_Value=72000000
RCC.FCLKCortexFreq_Value=72000000
RCC.FamilyName=M
RCC.HCLKFreq_Value=72000000
RCC.IPParameters=ADCFreqValue,AHBFreq_Value,APB1CLKDivider,APB1Freq_Value,APB1TimFreq_Value,APB2Freq_Value,APB2TimFreq_Value,FCLKCortexFreq_Value,FamilyName,HCLKFreq_Value,MCOFreq_Value,PLLCLKFreq_Value,PLLMCOFreq_Value,PLLMUL,PLLSourceVirtual,SYSCLKFreq_VALUE,SYSCLKSource,TimSysFreq_Value,USBFreq_Value,VCOOutput2Freq_Value
RCC.MCOFreq_Value=72000000
RCC.PLLCLKFreq_Value=72000000
RCC.PLLMCOFreq_Value=36000000
RCC.PLLMUL=RCC_PLL_MUL9
RCC.PLLSourceVirtual=RCC_PLLSOURCE_HSE
RCC.SYSCLKFreq_VALUE=72000000
RCC.SYSCLKSource=RCC_SYSCLKSOURCE_PLLCLK
RCC.TimSysFreq_Value=72000000
RCC.USBFreq_Value=72000000
RCC.VCOOutput2Freq_Value=8000000
SH.S_TIM1_CH1.0=TIM1_CH1,Encoder_Interface
SH.S_TIM1_CH1.ConfNb=1
SH.S_TIM1_CH2.0=TIM1_CH2,Encoder_Interface
SH.S_TIM1_CH2.ConfNb=1
SH.S_TIM4_CH3.0=TIM4_CH3,PWM Generation3 CH3
SH.S_TIM4_CH3.ConfNb=1
TIM1.EncoderMode=TIM_ENCODERMODE_TI12
TIM1.IC1Polarity=TIM_ICPOLARITY_FALLING
TIM1.IC2Polarity=TIM_ICPOLARITY_FALLING
TIM1.IPParameters=EncoderMode,IC2Polarity,IC1Polarity
TIM2.IPParameters=Period,Prescaler
TIM2.Period=65535
TIM2.Prescaler=5-1
TIM3.IPParameters=Prescaler,Period
TIM3.Period=40-1
TIM3.Prescaler=36000-1
TIM4.Channel-PWM\ Generation3\ CH3=TIM_CHANNEL_3
TIM4.IPParameters=Channel-PWM Generation3 CH3,Prescaler,Period,Pulse-PWM Generation3 CH3
TIM4.Period=800-1
TIM4.Prescaler=9-1
TIM4.Pulse-PWM\ Generation3\ CH3=400-1
VP_SYS_VS_Systick.Mode=SysTick
VP_SYS_VS_Systick.Signal=SYS_VS_Systick
VP_TIM2_VS_ClockSourceINT.Mode=Internal
VP_TIM2_VS_ClockSourceINT.Signal=TIM2_VS_ClockSourceINT
VP_TIM3_VS_ClockSourceINT.Mode=Internal
VP_TIM3_VS_ClockSourceINT.Signal=TIM3_VS_ClockSourceINT
board=custom
isbadioc=false

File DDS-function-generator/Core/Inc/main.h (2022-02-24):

/* USER CODE BEGIN Header */
/**
  ******************************************************************************
  * @file           : main.h
  * @brief          : Header for main.c file.
  *                   This file contains the common defines of the application.
  ******************************************************************************
  * @attention
  *
  * <h2><center>&copy; Copyright (c) 2022 STMicroelectronics.
  * All rights reserved.</center></h2>
  *
  * This software component is licensed by ST under BSD 3-Clause license,
  * the "License"; You may not use this file except in compliance with the
  * License. You may obtain a copy of the License at:
  *                        opensource.org/licenses/BSD-3-Clause
  *
  ******************************************************************************
  */
/* USER CODE END Header */

/* Define to prevent recursive inclusion -------------------------------------*/
#ifndef __MAIN_H
#define __MAIN_H

#ifdef __cplusplus
extern "C" {
#endif

/* Includes ------------------------------------------------------------------*/
#include "stm32f1xx_hal.h"

/* Private includes ----------------------------------------------------------*/
/* USER CODE BEGIN Includes */

/* USER CODE END Includes */

/* Exported types ------------------------------------------------------------*/
/* USER CODE BEGIN ET */

/* USER CODE END ET */

/* Exported constants --------------------------------------------------------*/
/* USER CODE BEGIN EC */

/* USER CODE END EC */

/* Exported macro ------------------------------------------------------------*/
/* USER CODE BEGIN EM */

/* USER CODE END EM */

/* Exported functions prototypes ---------------------------------------------*/
void Error_Handler(void);

/* USER CODE BEGIN EFP */

/* USER CODE END EFP */

/* Private defines -----------------------------------------------------------*/
#define DAC0_Pin GPIO_PIN_0
#define DAC0_GPIO_Port GPIOA
#define DAC1_Pin GPIO_PIN_1
#define DAC1_GPIO_Port GPIOA
#define DAC2_Pin GPIO_PIN_2
#define DAC2_GPIO_Port GPIOA
#define DAC3_Pin GPIO_PIN_3
#define DAC3_GPIO_Port GPIOA
#define DAC4_Pin GPIO_PIN_4
#define DAC4_GPIO_Port GPIOA
#define DAC5_Pin GPIO_PIN_5
#define DAC5_GPIO_Port GPIOA
#define DAC6_Pin GPIO_PIN_6
#define DAC6_GPIO_Port GPIOA
#define DAC7_Pin GPIO_PIN_7
#define DAC7_GPIO_Port GPIOA
#define ENC_BTN_Pin GPIO_PIN_10
#define ENC_BTN_GPIO_Port GPIOA
/* USER CODE BEGIN Private defines */

/* USER CODE END Private defines */

#ifdef __cplusplus
}
#endif

#endif /* __MAIN_H */

/************************ (C) COPYRIGHT STMicroelectronics *****END OF FILE****/

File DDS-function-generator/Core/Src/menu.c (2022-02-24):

/*
 * menu.c
 *
 *  Created on: Feb 1, 2022
 *      Author: bojan
 */

#include "menu.h"
#include <stdio.h>

/**************************
 * Menu interface functions
 **************************/

/********************************
 * Initialize the menu structure
 ********************************/
void Menu_Init(Menu *menu, SSD1306 *display, const volatile RotaryEncoder *encoder, DDS *dds) {
	menu->display = display;
	menu->encoder = encoder;
	menu->dds = dds;

	menu->prevState = MENU_ENTRY;
	menu->pos = WAVETYPE;

	Menu_UpdateDisplay(menu);
}

/********************************
 * Update every instance affected
 * by menu change: the display
 * and dds parameters
 ********************************/
void Menu_Update(Menu *menu) {
	// first determine the next menu state
	MenuState nextState = Menu_NextState(menu);
	// update the dds parameters
	Menu_UpdateDDS(menu, nextState);
	// update the display
	if(menu->change) {
		Menu_UpdateDisplay(menu);
	}
	// set nextState as prevState
	menu->prevState = nextState;
}


/****************************
 * Determine the next menu
 * state
 ****************************/
MenuState Menu_NextState(Menu *menu) {
	// stay in the previous state by default
	MenuState nextState = menu->prevState;
	// record if any change was made
	menu->change = menu->encoder->change || menu->encoder->btnChange;
	// determine the next state
	switch(menu->prevState) {
		case MENU_ENTRY:
			if(menu->encoder->change) {
				menu->change = 1;
				if(menu->encoder->rotationSpeed < 0 && menu->pos > 0) {
					menu->pos--;
				}
				else if(menu->encoder->rotationSpeed > 0 && menu->pos < MAX_MENU_ENTRY) {
					menu->pos++;
				}
			} else if(menu->encoder->btnChange) {
				switch(menu->pos) {
					// waveform type change
					case 0:
						nextState = WAVETYPE_CHANGE;
					break;
					// waveform frequency change
					case 1:
						nextState = FREQUENCY_CHANGE;
					break;
					// waveform amplitude change
					case 2:
						nextState = AMPLITUDE_CHANGE;
					break;
					// waveform type change
					case 3:
						nextState = STATE_CHANGE;
					break;
					default:
					break;
				}
			}
		break;
		case WAVETYPE_CHANGE:
		case FREQUENCY_CHANGE:
		case AMPLITUDE_CHANGE:
		case STATE_CHANGE:
			if(menu->encoder->btnChange) {
				nextState = UPDATE_CHANGES;
			}
		break;
		case UPDATE_CHANGES:
			nextState = MENU_ENTRY;
		break;
		default:
		break;
	}
	return nextState;
}

/****************************
 * Update DDS parameters
 ****************************/
void Menu_UpdateDDS(Menu *menu, MenuState nextState) {
	if(menu->change) {
		// first, check if rotary encoder changed
		if(menu->encoder->change) {
			// next, check if waveform type should be changed
			if(	menu->prevState == WAVETYPE_CHANGE &&
				nextState == WAVETYPE_CHANGE) {
				switch(menu->dds->waveType) {
					case SINE:
						DDS_ChangeWaveform(menu->dds, SQUAREWAVE_LUT, SQUAREWAVE_LUT_SIZE, SQUARE);
					break;
					case SQUARE:
						DDS_ChangeWaveform(menu->dds, TRIANGLEWAVE_LUT, TRIANGLEWAVE_LUT_SIZE, TRIANGLE);
					break;
					case TRIANGLE:
						DDS_ChangeWaveform(menu->dds, SAWTOOTHWAVE_LUT, SAWTOOTHWAVE_LUT_SIZE, SAWTOOTH);
					break;
					case SAWTOOTH:
						DDS_ChangeWaveform(menu->dds, SINEWAVE_LUT, SINEWAVE_LUT_SIZE, SINE);
					break;
					default:
					break;
				}
			}
			// check if frequency should be changed
			else if(menu->prevState == FREQUENCY_CHANGE &&
					nextState == FREQUENCY_CHANGE) {
				uint32_t absSpeed = (menu->encoder->rotationSpeed > 0) ? menu->encoder->rotationSpeed : -menu->encoder->rotationSpeed;
				int8_t sign = (menu->encoder->rotationSpeed > 0) ? 1 : -1;
				if(absSpeed <= 10000) {
					DDS_ChangeFrequency(menu->dds, menu->dds->freq + sign*1);
				} else {
					DDS_ChangeFrequency(menu->dds, menu->dds->freq + sign*100);
				}
			}
			// check if amplitude should be changed
			else if(menu->prevState == AMPLITUDE_CHANGE &&
							nextState == AMPLITUDE_CHANGE) {
				uint32_t absSpeed = (menu->encoder->rotationSpeed > 0) ? menu->encoder->rotationSpeed : -menu->encoder->rotationSpeed;
				int8_t sign = (menu->encoder->rotationSpeed > 0) ? 1 : -1;
				if(absSpeed <= 8000) {
					DDS_ChangeAmplitude(menu->dds, menu->dds->amp + sign*10);
				} else {
					DDS_ChangeAmplitude(menu->dds, menu->dds->amp + sign*100);
				}
			}
			// check if dds state should be changed
			else if(menu->prevState == STATE_CHANGE &&
							nextState == STATE_CHANGE) {
				if(menu->dds->running) {
					DDS_Stop(menu->dds);
				} else {
					DDS_Start(menu->dds);
				}
			}
		}
		// if UPDATE_CHANGES, update the dds
		else if(nextState == UPDATE_CHANGES) {
			DDS_Update(menu->dds);
		}
	}
}
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
